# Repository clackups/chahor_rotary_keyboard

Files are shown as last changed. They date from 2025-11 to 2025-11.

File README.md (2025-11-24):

Chahor, an experimental keyboard for a user with cerebral palsy
===============================================================

This is an experimental keyboard aiming to improve the typing speed
for a PC user with cerebral palsy.

Requirements:

* one keypress at a time, one working hand;

* keys located compactly, reducing the need to move the hand;

* fully compatible PC keyboard, no additional software on the computer.

How it works:

The user chooses a letter from a layer, either by rotating a rotary
encoder wheel, or by pressing the navigation buttons. Then, by
pressing one of the text entry keys, the required symbol is sent to
the computer.

A small OLED screen shows the current letter or symbol that is ready
to send to the computer.

The keyboard has currently 4 symbol layers:

* English alphabet;

* Ukrainian alphabet;

* Numbers and special symbols as they are located on a US-English
  keyboard (`1` and `!` on the first number key, `0` and `)` on the
  last one);

* Function keys F1 to F12.

Six text entry keys are as follows:

* lower-case letter (or a number in the numeric layer);

* upper-case letter (or a symbol in the numeric layer);

* spacebar (on a long press, it works as the Enter key);

* backspace;

* Ctrl (on a long press, it works as Alt key);

* switch between layers.

The two navigation keys complement the rotary encoder and allow moving
forward and back along the alphabet. On a long press, the alphabet is
scrolled automatically at 3 letters per second.

Switching between languages
---------------------------

The firmware is preprogrammed to send the following combinations to
the host for language switching:

* US English: `Ctrl+Shift+1`
* Ukrainian:  `Ctrl+Shift+4`

These combinations are easy to set in Windows language preferences.

In Ubuntu, a Gnome extension called Shyriiwook needs to be installed:

```
git clone https://github.com/madhead/shyriiwook.git
cd shyriiwook
make install
gnome-extensions enable shyriiwook@madhead.me
```

After the extension is installed and activated, it should show the list of available keyboarrd layouts:

```
$ gdbus introspect --session --dest org.gnome.Shell --object-path /me/madhead/Shyriiwook --only-properties
node /me/madhead/Shyriiwook {
  interface me.madhead.Shyriiwook {
    properties:
      readonly as availableLayouts = ['us', 'ua'];
      readonly s currentLayout = 'us';
  };
};
```

The following two commands would activate the Ukrainian and US layouts, correspondinigly:

```
gdbus call --session --dest org.gnome.Shell --object-path /me/madhead/Shyriiwook --method me.madhead.Shyriiwook.activate "ua"

gdbus call --session --dest org.gnome.Shell --object-path /me/madhead/Shyriiwook --method me.madhead.Shyriiwook.activate "us"
```

Once it works, you can assign keyboard shortcuts to execute these
commands. In Settings -> Keyboard -> Keyboard Shortcuts -> Custom
Shortcuts, define the shortcuts as indicated above, to execute the
Gnome extension calls.

Firmware
--------

The firmawe is tested with RP2040, using Waveshare RP2040-Tiny for
production, and RP2040 Pico for development.

The firmware is written in Rust and it needs the following preparation
steps. The following instructions are suitable for ubuntu or Debian.

Environment preparation:

```
# the firmware build user needs to belong to the plugdev group in
# order to be able to upload the firmware to the board.
sudo usermod -aG plugdev $LOGNAME

# pre-requisites for building the firmware:
sudo apt-get install -y git build-essential

# install probe-rs udev rules
sudo wget https://probe.rs/files/69-probe-rs.rules -o /etc/udev/rules.d/69-probe-rs.rules
sudo udevadm control --reload
# if the debugger is already conneected to a USB port, re-initialize udev:
sudo udevadm trigger

# Follow the instructions at https://rustup.rs/ and install Rust:
curl --proto '=https' --tlsv1.2 -sSf https://sh.rustup.rs | sh

# re-login so that environment variables and plugdev group membership take effect

# Add the rp2040 compiler support:
rustup target add thumbv6m-none-eabi

# install probe-rs (only if debugger board is used)
curl --proto '=https' --tlsv1.2 -LsSf https://github.com/probe-rs/probe-rs/releases/latest/download/probe-rs-tools-installer.sh | sh

# install cargo-make
cargo install cargo-make

# get the firmware code
git clone https://github.com/clackups/chahor_rotary_keyboard.git
cd chahor_rotary_keyboard/firmware/
```

If you need to develop and debug the firmware, it is recommended to
use two RP2040 Pico boards: one will run the Chahor firmware, and the
other will be used as a debug probe. See the [instructions for the
probe](https://www.raspberrypi.com/documentation/microcontrollers/debug-probe.html)
for more details.

With the debugger connected, use the following commands to compile and upload the firmware:

```
# compile the firmware
cargo make build-dev

# compile and upload the firmware, using the debug board
cargo make run-dev
```

If you only need to upload a new version of the firmware, boot the
RP2040 board while the BOOT button is pressed, then

```
cargo make rr
```

If the load is successful, the keyboard is ready for work. You may
disconnect the debugger cable until you need to load the firmnmware
again.

Assembly
--------

Bill of material:

* [Waveshare RP2040-Tiny](https://www.waveshare.com/rp2040-tiny.htm)

* 8 low-profile MX keyboard switches

* 8 low-profile keyboard keycaps

* 24-pulse [rotary encoder by Adafruit](https://www.adafruit.com/product/377)

* 0.96" OLED screen with i2c interface by [Lilygo or the like](https://lilygo.cc/products/0-96-inch-oled)

* 8 M2*8mm screws and nuts

* 4 M2*16mm screws and nuts

* 0.9mm single-core copper wire

* connecting wires

* 4 round self-adhesive silicone bumpers, 12mm

3D printing models for the body and the bottom plate are [available in 3D_Print folder](3D_Print/), alongside with FreeCad models.

KiCad schematics source and the PDF are available in [KiCad folder](KiCad/).

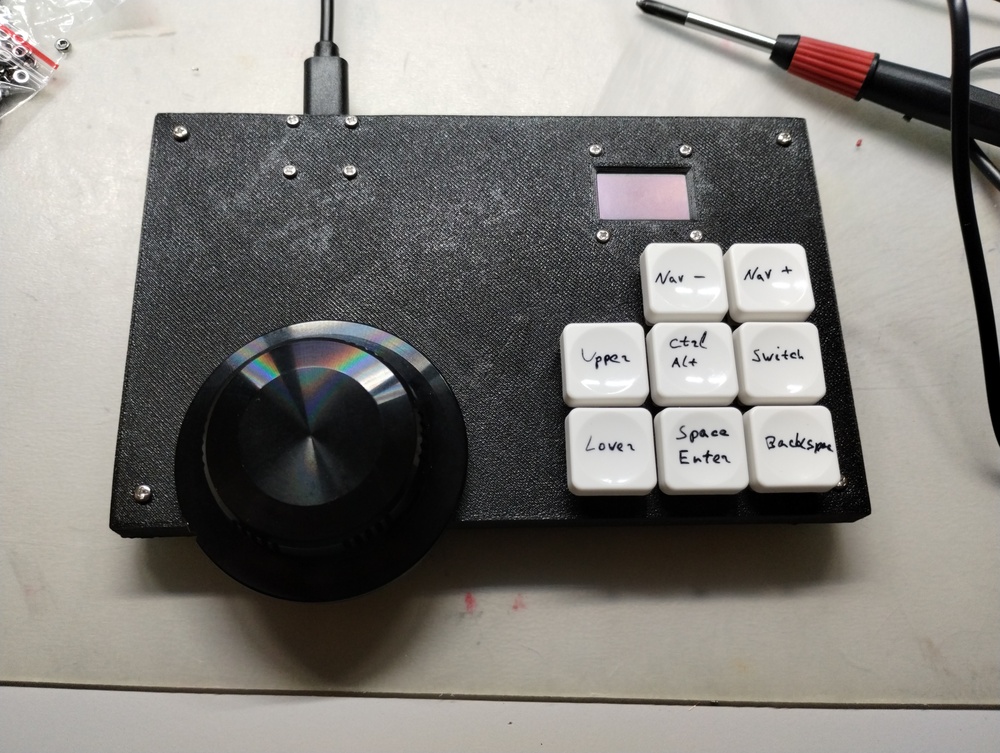
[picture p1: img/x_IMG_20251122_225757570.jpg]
Top view


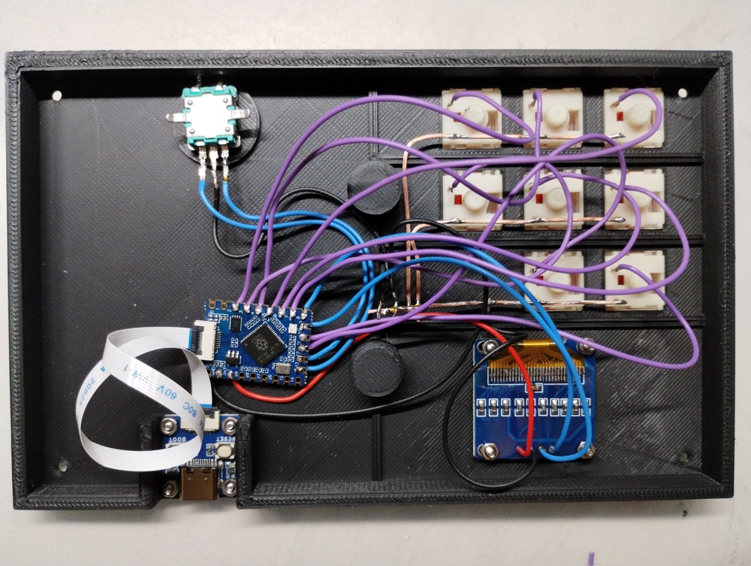
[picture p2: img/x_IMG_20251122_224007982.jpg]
Wiring top view


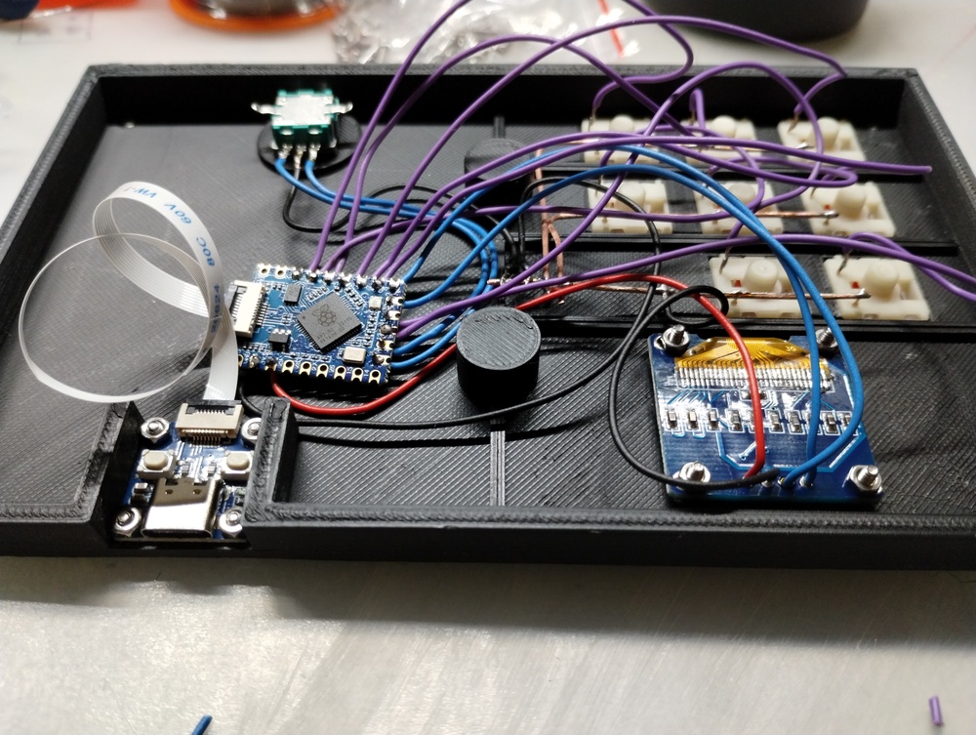
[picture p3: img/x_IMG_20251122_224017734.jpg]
Wiring side view


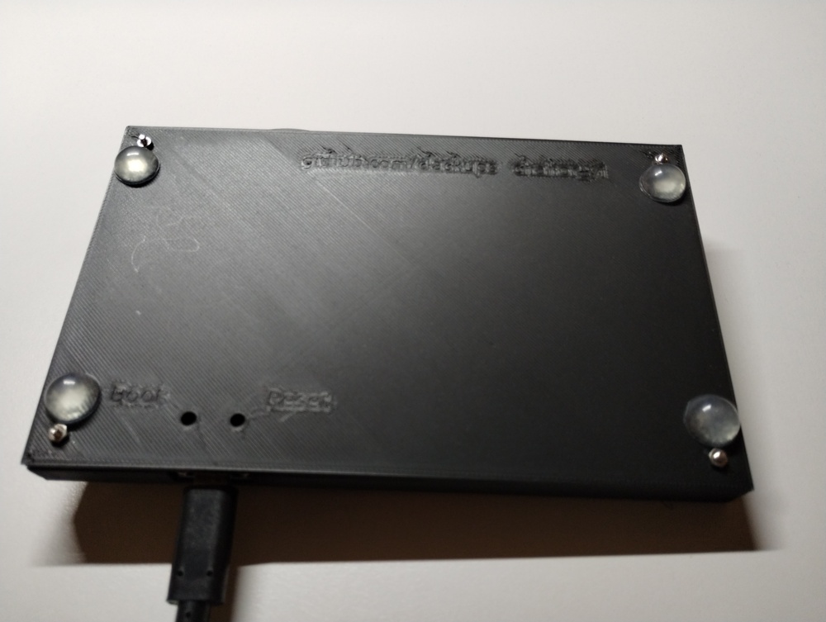
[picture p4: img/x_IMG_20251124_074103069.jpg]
Bottom view


## Copyright and license

This work is licensed under the MIT License.

Copyright (c) 2025 clackups@gmail.com

Fediverse: [@clackups@social.noleron.com](https://social.noleron.com/@clackups)

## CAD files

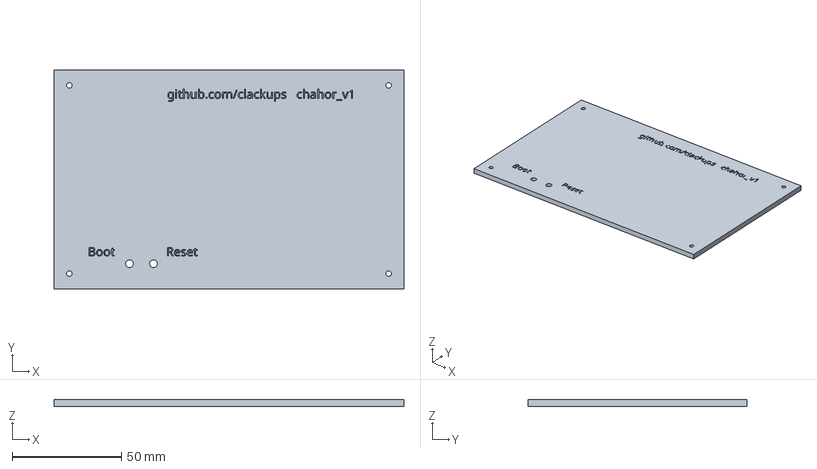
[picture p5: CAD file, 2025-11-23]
3D_Print/chahor_bottom_plate-Body.3mf
160.0 x 100.0 x 3.00 mm

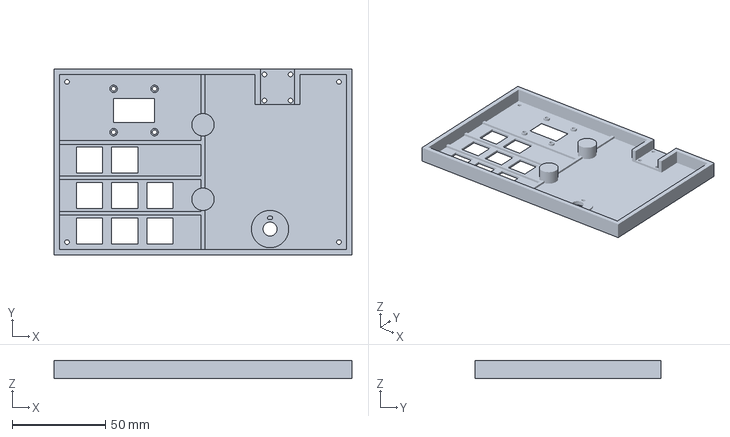
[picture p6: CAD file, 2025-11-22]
3D_Print/chahor_top_plate-Body.3mf
160.0 x 100.0 x 9.90 mm

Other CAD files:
3D_Print/chahor_bottom_plate.FCStd
3D_Print/chahor_top_plate.FCStd

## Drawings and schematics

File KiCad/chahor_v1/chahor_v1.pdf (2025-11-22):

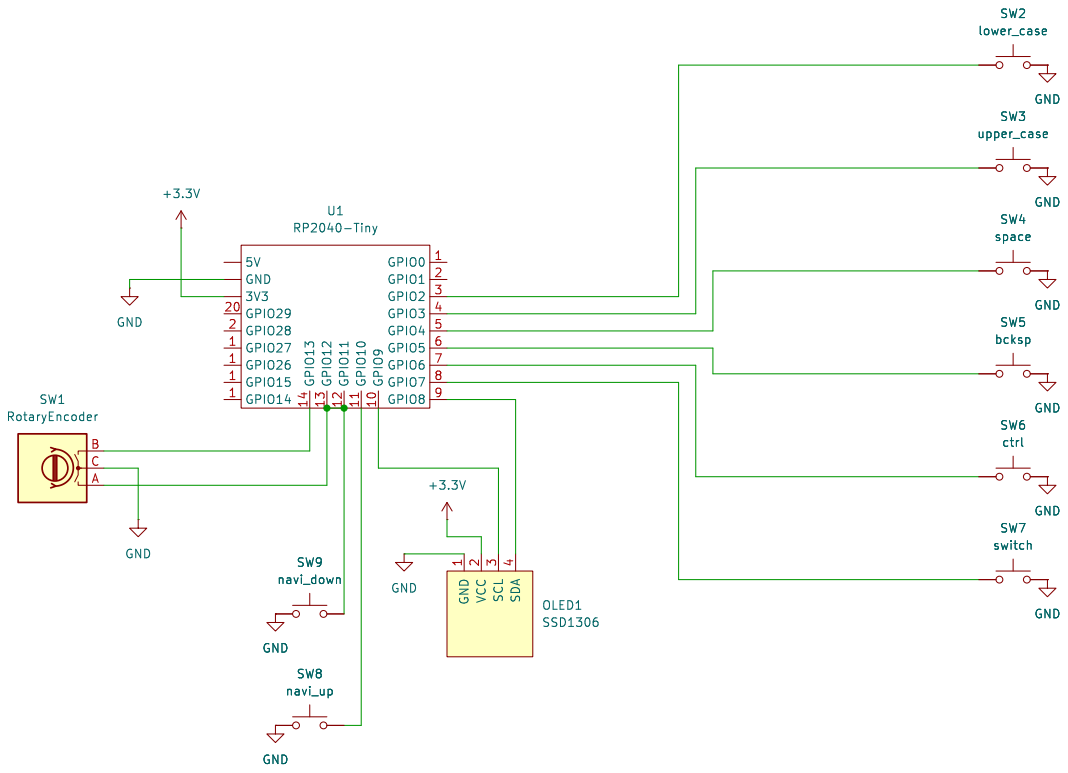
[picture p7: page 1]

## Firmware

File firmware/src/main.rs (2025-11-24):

#![no_std]
#![no_main]

mod constants;
use constants::*;

use defmt::*;
use embassy_executor::{Executor};
use embassy_rp::bind_interrupts;
use embassy_rp::i2c::{self, Async, Config};
use embassy_rp::multicore::{spawn_core1, Stack};
use embassy_rp::peripherals::{I2C0};
use embassy_rp::gpio::{Input, Pull};
use embassy_sync::blocking_mutex::raw::CriticalSectionRawMutex;
use embassy_sync::channel::Channel;
use embassy_time::{Timer, Instant};
use ssd1306::mode::DisplayConfig;
use ssd1306::prelude::DisplayRotation;
use ssd1306::size::DisplaySize128x64;
use ssd1306::{I2CDisplayInterface, Ssd1306};
use static_cell::StaticCell;

use rotary_encoder_hal::{Direction, Rotary};

mod keymaps;
use keymaps::KEYMAPS;

mod usb_keyboard;
use crate::usb_keyboard::{UsbKeyboard, UsbKeyboardRequestHandler};
use embassy_rp::peripherals::USB;
use embassy_rp::usb::{Driver};
use embassy_usb::UsbDevice;
use embassy_usb::class::hid::{HidReader, HidWriter};
use usbd_hid::descriptor::{KeyboardReport};
use usbd_hid::descriptor::KeyboardUsage as KU;

use embedded_graphics::{
    pixelcolor::BinaryColor,
    prelude::*,
};

use u8g2_fonts::{
    fonts,
    types::{FontColor, VerticalPosition},
    FontRenderer,
};

mod boards;
use boards::*;


use {defmt_rtt as _, panic_probe as _};

static mut CORE1_STACK: Stack<4096> = Stack::new();
static EXECUTOR0: StaticCell<Executor> = StaticCell::new();
static EXECUTOR1: StaticCell<Executor> = StaticCell::new();
static CHANNEL: Channel<CriticalSectionRawMutex, DisplayMessage, 20> = Channel::new();
static USB_KEYBOARD_CONFIG: StaticCell<usb_keyboard::Config> = StaticCell::new();


enum DisplayMessage {
    ShowChars([char; 3]),
}

bind_interrupts!(struct Irqs {
    I2C0_IRQ => i2c::InterruptHandler<I2C0>;
    USBCTRL_IRQ => embassy_rp::usb::InterruptHandler<USB>;
});


#[cortex_m_rt::entry]
fn main() -> ! {
    let p = embassy_rp::init(Default::default());
    let r = split_resources!(p);

    // Set up I2C0 for the SSD1306 OLED Display
    let i2c0 = i2c::I2c::new_async(r.screen.peri, r.screen.scl, r.screen.sda, Irqs, Config::default());
    // display task
    spawn_core1(
        p.CORE1,
        unsafe { &mut *core::ptr::addr_of_mut!(CORE1_STACK) },
        move || {
            let executor1 = EXECUTOR1.init(Executor::new());
            executor1.run(|spawner| unwrap!(spawner.spawn(core1_task(i2c0))));
        },
    );

    debug!("Create USB keyboard device");
    let usb_driver = Driver::new(p.USB, Irqs);
    let usb_keyboard_config = USB_KEYBOARD_CONFIG.init(usb_keyboard::Config::new());
    let usb_keyboard = UsbKeyboard::new(usb_keyboard_config, usb_driver);

    let executor0 = EXECUTOR0.init(Executor::new());
    executor0.run(|spawner| {
        spawner.spawn(usb_run(usb_keyboard.usb)).unwrap();
        spawner.spawn(hid_read(usb_keyboard.hid_reader, usb_keyboard.request_handler)).unwrap();
        spawner.spawn(core0_task(r.rotary_enc, r.buttons, usb_keyboard.hid_writer)).unwrap();
    });
}


#[embassy_executor::task]
async fn usb_run(mut usb: UsbDevice<'static, Driver<'static, USB>>) {
    debug!("Start 'USB Run' task");
    usb.run().await;
}

#[embassy_executor::task]
async fn hid_read(
    hid_reader: HidReader<'static, Driver<'static, USB>, 1>,
    request_handler: &'static mut UsbKeyboardRequestHandler,
) {
    debug!("Start 'HID Read' task");
    hid_reader.run(false, request_handler).await;
}


// Keyboard task

#[embassy_executor::task]
async fn core0_task(rotary_enc: RotaryEncResources, buttons: ButtonResources,
                    mut hid_writer: HidWriter<'static, Driver<'static, USB>, 8>) {
    debug!("Hello from core 0");

    let mut enc = Rotary::new(Input::new(rotary_enc.pin_a, Pull::Up), Input::new(rotary_enc.pin_b, Pull::Up));
    let navi_up = Input::new(buttons.navi_up, Pull::Up);
    let navi_down = Input::new(buttons.navi_down, Pull::Up);
    let lower_case = Input::new(buttons.lower_case, Pull::Up);
    let upper_case = Input::new(buttons.upper_case, Pull::Up);
    let space = Input::new(buttons.space, Pull::Up);
    let bcksp = Input::new(buttons.bcksp, Pull::Up);
    let ctrl = Input::new(buttons.ctrl, Pull::Up);
    let switch = Input::new(buttons.switch, Pull::Up);

    let mut enc_pos: i32 = 0;
    let mut navi_updown: i32 = 0;
    let mut navi_button_pressed: i32 = 0;
    let mut navi_repeat_timer = Instant::now();
    let mut keymap_n: usize = 0;
    let mut keymap_pos: usize = 0;
    let mut ks: &keymaps::KS = &KEYMAPS[keymap_n][keymap_pos];
    let mut updated = true;
    let mut button_released = true;
    let mut maybe_long_press = false;
    let mut long_press_start = Instant::now();
    let mut special_ks = KU::KeyboardErrorUndefined;
    let mut with_ctrl = false;
    let mut with_alt = false;

    loop {
        let mut keymap_delta: i32 = 0;

        match enc.update().unwrap() {
            Direction::Clockwise => {
                enc_pos += 1;
                if enc_pos >= ROTARY_SCALE_FACTOR {
                    enc_pos = 0;
                    keymap_delta = 1;
                    updated = true;
                }
            }
            Direction::CounterClockwise => {
                enc_pos -= 1;
                if enc_pos <= ROTARY_SCALE_FACTOR * -1 {
                    enc_pos = 0;
                    keymap_delta = -1;
                    updated = true;
                }
            }
            Direction::None => {
            }
        }

        if navi_updown != 0 {
            keymap_delta = navi_updown;
            navi_updown = 0;
            updated = true;
        }

        if updated {
            if keymap_delta > 0 {
                keymap_pos += keymap_delta as usize;
                if keymap_pos >= 40 || KEYMAPS[keymap_n][keymap_pos].c == KU::KeyboardErrorUndefined {
                    keymap_pos = 0;
                }
            }
            else if keymap_delta < 0 {
                if keymap_pos == 0 {
                    keymap_pos = 39;
                    while KEYMAPS[keymap_n][keymap_pos].c == KU::KeyboardErrorUndefined {
                        keymap_pos -= 1;
                    }
                }
                else {
                    keymap_pos -= (keymap_delta * -1) as usize;
                }
            }

            ks = &KEYMAPS[keymap_n][keymap_pos];
            if ks.c == KU::KeyboardErrorRollOver {
                let ksc = &keymaps::COMPLEX_KEYMAPS[ks.s[0] as usize];
                CHANNEL.send(DisplayMessage::ShowChars(ksc.display_str)).await;
            }
            else {
                CHANNEL.send(DisplayMessage::ShowChars(ks.s)).await;
            }
            updated = false;
        }

        let mut button_down = false;
        let mut long_press_button_down = false;
        let mut send_letter = false;
        let mut with_shift = false;
        let mut special_ks_button_down = false;
        let mut send_special_ks = false;
        let mut switch_pressed = false;
        let mut ctrl_button_down = false;

        if navi_up.is_low() {
            long_press_button_down = true;
            navi_button_pressed = 1;
            button_down = true;
        }
        if navi_down.is_low() {
            long_press_button_down = true;
            navi_button_pressed = -1;
            button_down = true;
        }
        if lower_case.is_low() {
            send_letter = true;
            button_down = true;
        }
        else if upper_case.is_low() {
            send_letter = true;
            with_shift = true;
            button_down = true;
        }
        else if space.is_low() {
            special_ks = KU::KeyboardSpacebar;
            button_down = true;
            long_press_button_down = true;
        }
        else if bcksp.is_low() {
            special_ks = KU::KeyboardBackspace;
            special_ks_button_down = true;
            button_down = true;
        }
        else if ctrl.is_low() {
            long_press_button_down = true;
            ctrl_button_down = true;
            button_down = true;
        }
        else if switch.is_low() {
            switch_pressed = true;
            button_down = true;
        }

        let mut send_report = false;

        if button_released {
            if button_down {
                button_released = false;
                if long_press_button_down {
                    maybe_long_press = true;
                    long_press_start = Instant::now();
                    if ctrl_button_down {
                        debug!("ctrl_button_down");
                        with_ctrl = true;
                    }
                }
                else if switch_pressed {
                    keymap_n += 1;
                    if keymap_n >= KEYMAPS.len() {
                        keymap_n = 0;
                    }

                    // if switching between keymaps landed on the null key, move back to the last symbol
                    if KEYMAPS[keymap_n][keymap_pos].c == KU::KeyboardErrorUndefined {
                        while KEYMAPS[keymap_n][keymap_pos].c == KU::KeyboardErrorUndefined {
                            keymap_pos -= 1;
                        }
                    }

                    if keymaps::KEYMAP_PRELUDES[keymap_n].0 {
                        let mut report = KeyboardReport {
                            leds: 0,
                            modifier: keymaps::KEYMAP_PRELUDES[keymap_n].1,
                            reserved: 0,
                            keycodes: [keymaps::KEYMAP_PRELUDES[keymap_n].2 as u8, 0, 0, 0, 0, 0],
                        };
                        send_report_to_writer(&mut hid_writer, &report).await;
                        report = KeyboardReport {
                            leds: 0,
                            modifier: 0,
                            reserved: 0,
                            keycodes: [0, 0, 0, 0, 0, 0],
                        };
                        send_report_to_writer(&mut hid_writer, &report).await;
                    }
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

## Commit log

2025-11-10 reorganized the folders and added the body 3d print
    [chahor_top_plate.FCStd]
2025-11-11 top plate: bigger holes and other improvements
    [chahor_top_plate-Body.3mf, chahor_top_plate.FCStd]
2025-11-12 top plate: fixed wrong holes, lowered the ribs
    [chahor_top_plate-Body.3mf, chahor_top_plate.FCStd]
2025-11-12 added the bottom plate
    [chahor_bottom_plate-Body.3mf, chahor_bottom_plate.FCStd]
2025-11-15 added Kicad schematics
    [chahor_v1.kicad_pcb, chahor_v1.kicad_sch]
2025-11-17 bottom plate 3mm thick
    [chahor_bottom_plate-Body.3mf, chahor_bottom_plate.FCStd]
2025-11-20 moved the rotary encoder closer to the keys
    [chahor_top_plate-Body.3mf, chahor_top_plate.FCStd]
2025-11-22 improved rotary encoder placement
    [chahor_top_plate-Body.3mf, chahor_top_plate.FCStd]
2025-11-22 redesigned the top plate for waveshare RP2040-Tiny
    [chahor_top_plate-Body.3mf, chahor_top_plate.FCStd]
2025-11-22 bottom plate with pillars and screw holes
    [chahor_bottom_plate-Body.3mf, chahor_bottom_plate.FCStd, chahor_top_plate.FCStd]
2025-11-22 changed the production board to RP2040-Tiny
    [chahor_v1.kicad_sch]
2025-11-22 changed the body and schematics for Waveshare RP2040-Tiny
    [chahor_bottom_plate-Body.3mf, chahor_bottom_plate.FCStd, chahor_top_plate-Body.3mf, chahor_top_plate.FCStd]
2025-11-23 Bottom plate: RP2040 button holes and text embossing
    [chahor_bottom_plate-Body.3mf, chahor_bottom_plate.FCStd]
